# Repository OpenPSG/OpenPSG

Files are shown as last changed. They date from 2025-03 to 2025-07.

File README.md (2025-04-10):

# OpenPSG

A [FOSS](https://www.gnu.org/philosophy/free-sw.en.html) Polysomnography Platform For Sleep Research.

## Philosophy

* **Cost is Critical** (off-the-shelf, commodity components).
* **Less is More** (if one sensor can do the job of two, use it).
* **Easy to Use** (no complex setup/prep work).
* **Modular** (mix and match sensors).
* **Open Source** (hardware and software).
* **Open Data** (no proprietary formats).

## Disclaimer

OpenPSG is not intended to diagnose, treat, cure, or prevent any medical 
condition. It is designed for research purposes only and should not be used as 
a substitute for professional medical advice or care. Users are responsible for
ensuring compliance with the relevant regulations and standards in their region.

Hardware evaluation boards and kits are provided for use in engineering 
development, demonstration, or evaluation purposes only. They are not considered 
by the OpenPSG authors to be finished end-products fit for general consumer use.

All users are expected to have the necessary knowledge and experience to use the 
hardware and software safely and effectively. The OpenPSG authors are not 
responsible for any injuries, damages, or losses resulting from the use of the
hardware or software.

## License

All software is licensed under the [GNU Affero General Public License v3.0](https://www.gnu.org/licenses/agpl-3.0.html). 
All hardware designs are licensed under the [CERN Open Hardware License v2 - Strongly Reciprocal](https://ohwr.org/cern_ohl_s_v2.txt).

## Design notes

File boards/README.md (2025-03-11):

# Board Files

The boards are designed with/for KiCad v8.0.x

## JLCPCB Manufacturing and Assembly

### Gerbers and Drill Files

Follow the instructions here:

https://jlcpcb.com/help/article/how-to-generate-gerber-and-drill-files-in-kicad-8

### Bill of Materials (BOM)

In eeschema, go to `Tools` -> `Generate Bill of Materials`.

In the edit tab configure the fields as follows:

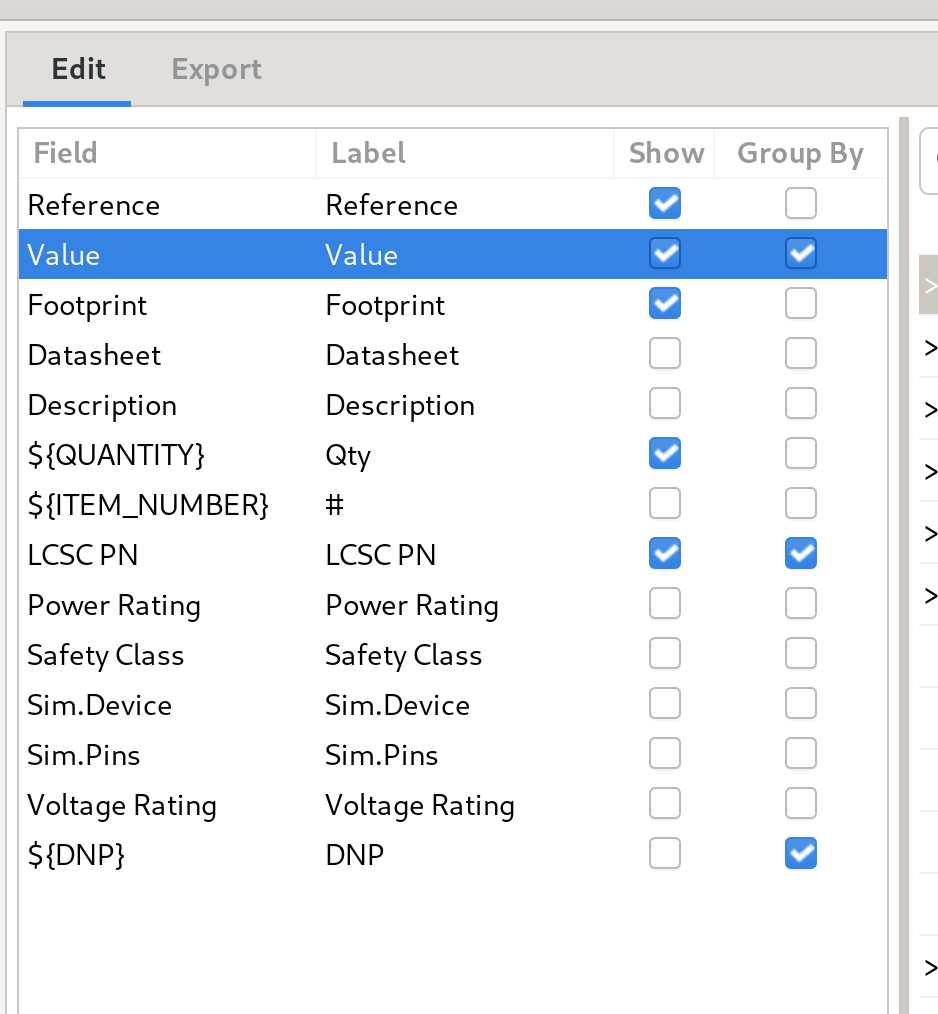
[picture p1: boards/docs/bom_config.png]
BOM configuration


Then click on `Generate` and save the file as `<board>-bom.csv` in the manufacturing files folder.

### Pick and Place (CPL)

In pcbnew, go to `File` -> `Fabrication Outputs` -> `Component Placement (.pos, .gbr)...`.

Configure the fields as follows:

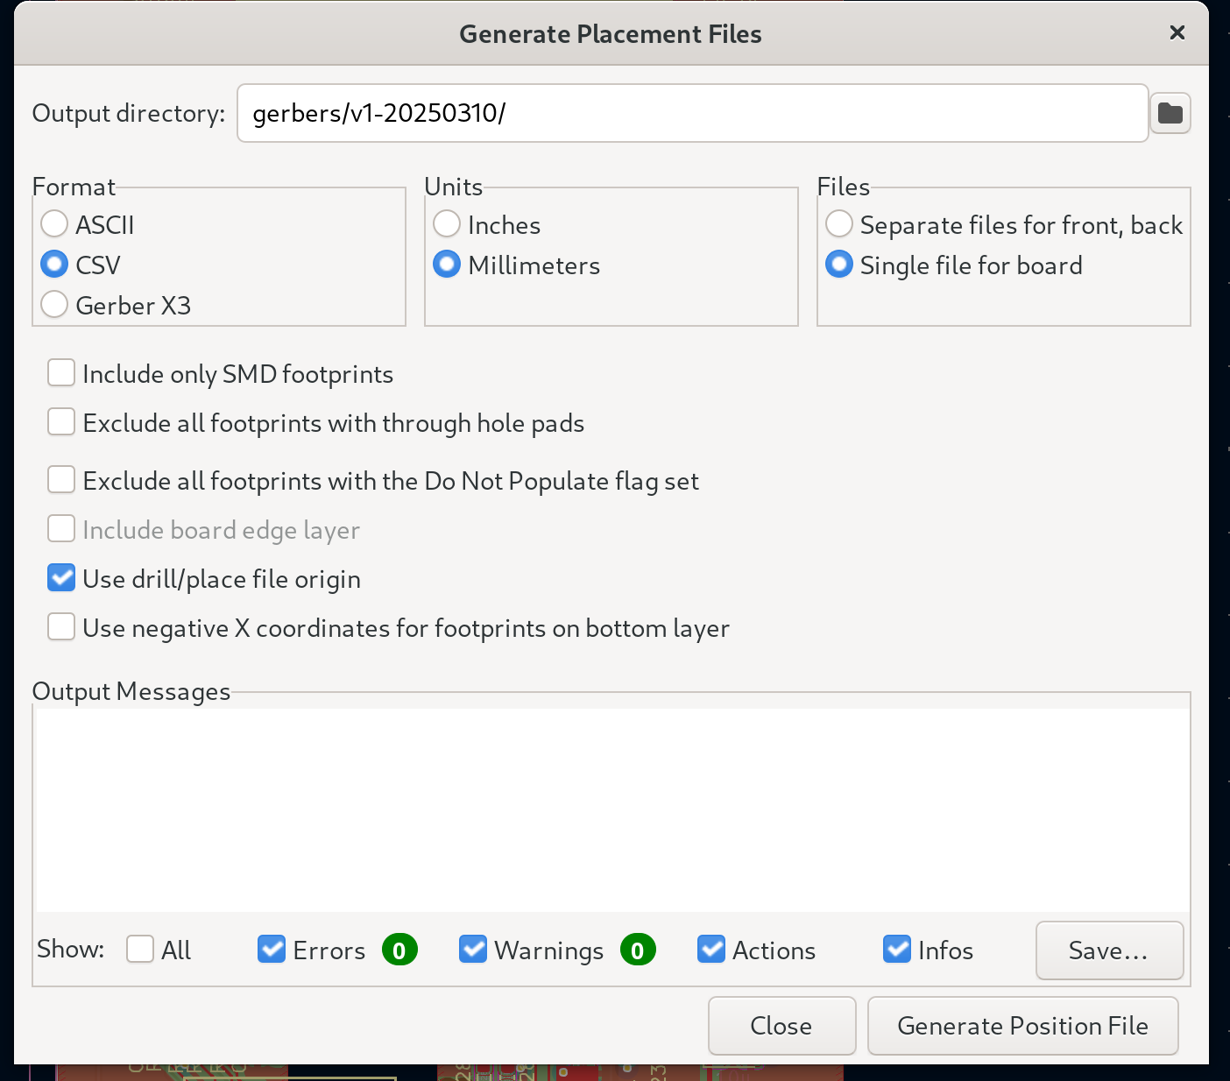
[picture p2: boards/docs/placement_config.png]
CPL configuration


Then click on `Generate`.

### Convert to JLCPCB Format

Use my [jlcfabtool](https://github.com/dpeckett/jlcfabtool) utility to convert the files to the JLCPCB format.

```sh
jlcfabtool bom convert <board>-bom.csv
jlcfabtool placement convert <board>-all-pos.csv
```

### Create the Archive

```sh
cd <board>
zip -r ../$(basename "$(pwd)").zip ./*
```

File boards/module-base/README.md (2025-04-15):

# Module Base

The starting point for all sensors / actuators.

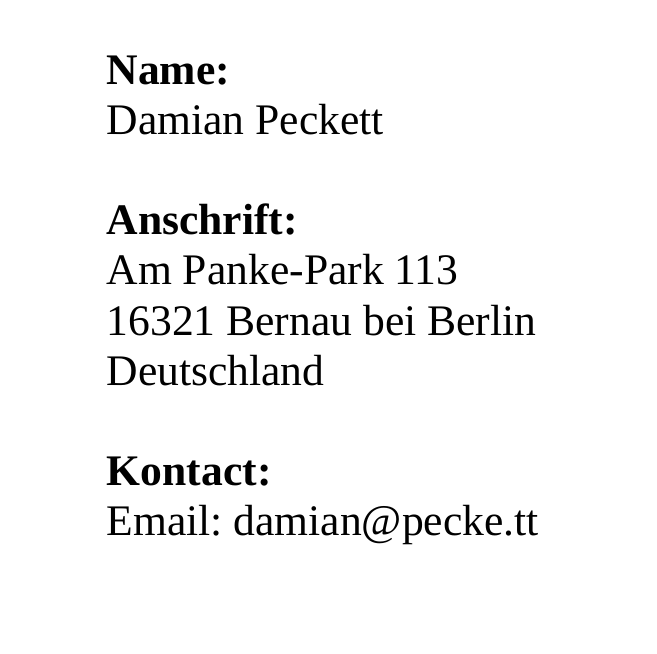
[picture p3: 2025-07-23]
public/images/contact.png

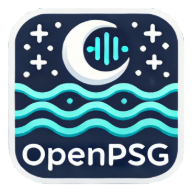
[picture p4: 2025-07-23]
public/web-app-manifest-192x192.png

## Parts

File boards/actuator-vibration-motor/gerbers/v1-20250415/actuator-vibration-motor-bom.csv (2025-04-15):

Reference | Value | Datasheet | Footprint | Qty | DNP | LCSC PN
C1,C4 | 1u | ~ | Capacitor_SMD:C_0402_1005Metric | 2 |  | C52923
C2,C3,C7 | 0.1u | ~ | Capacitor_SMD:C_0402_1005Metric | 3 |  | C1525
C5,C6 | 12p | ~ | Capacitor_SMD:C_0402_1005Metric | 2 |  | C1547
C8 | 1n | ~ | Capacitor_SMD:C_0402_1005Metric | 1 |  | C1523
D1 | 1N5819WS | https://datasheet.lcsc.com/lcsc/2204281430_Guangdong-Hottech-1N5819WS_C191023.pdf | Diode_SMD:D_SOD-323 | 1 |  | C191023
J1 | RS485 | ~ | Connector_JST:JST_PH_S4B-PH-K_1x04_P2.00mm_Horizontal | 1 |  | C2908636
J3 | Download | ~ | Connector_PinHeader_1.27mm:PinHeader_1x02_P1.27mm_Vertical | 1 |  | C703015
J4 | Vibration Motor | ~ | Connector_JST:JST_PH_S2B-PH-K_1x02_P2.00mm_Horizontal | 1 |  | C2908634
JP1 | Terminate | ~ | Jumper:SolderJumper-2_P1.3mm_Open_RoundedPad1.0x1.5mm | 1
Q1 | AO3400 | http://www.aosmd.com/pdfs/datasheet/AO3400A.pdf | Package_TO_SOT_SMD:SOT-23 | 1 |  | C20917
R1,R2 | 120 | ~ | Resistor_SMD:R_0402_1005Metric | 2 |  | C25079
U1 | AP2112K-3.3 | https://www.diodes.com/assets/Datasheets/AP2112.pdf | Package_TO_SOT_SMD:SOT-23-5 | 1 |  | C51118
U2 | COS13487E |  | Package_SO:SOP-8_3.9x4.9mm_P1.27mm | 1 |  | C22466040
U3 | STM32G031G8Ux | https://www.st.com/resource/en/datasheet/stm32g031g8.pdf | Package_DFN_QFN:QFN-28_4x4mm_P0.5mm | 1 |  | C432211
Y1 | 32.768k | ~ | Crystal:Crystal_SMD_3215-2Pin_3.2x1.5mm | 1 |  | C32346

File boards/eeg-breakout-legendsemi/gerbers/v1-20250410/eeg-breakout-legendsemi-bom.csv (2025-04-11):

Reference | Value | Datasheet | Footprint | Qty | DNP | LCSC PN
C1,C3,C5,C6,C9 | 1u | ~ | Capacitor_SMD:C_0402_1005Metric | 5 |  | C52923
C2,C4 | 0.1u | ~ | Capacitor_SMD:C_0402_1005Metric | 2 |  | C1525
C7,C10,C11,C12,C13,C14,C15,C16,C17,C18 | 1n | ~ | Capacitor_SMD:C_0402_1005Metric | 10 |  | C1523
C8 | 10u | ~ | Capacitor_SMD:C_0603_1608Metric | 1 |  | C19702
R1 | 1M | ~ | Resistor_SMD:R_0402_1005Metric | 1 |  | C26083
R2 | 100k | ~ | Resistor_SMD:R_0402_1005Metric | 1 |  | C25741
R3,R4,R5,R6,R7,R8,R9,R10,R11 | 2.2k | ~ | Resistor_SMD:R_0402_1005Metric | 9 |  | C25879
U1 | LH001-91Q40AR2 |  | Package_DFN_QFN:QFN-40-1EP_5x5mm_P0.4mm_EP3.6x3.6mm | 1 |  | C42459077

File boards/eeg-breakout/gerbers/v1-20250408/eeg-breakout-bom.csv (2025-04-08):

Reference | Value | Datasheet | Footprint | Qty | DNP | LCSC PN
C1,C4,C13 | 10u | ~ | Capacitor_SMD:C_0603_1608Metric | 3 |  | C19702
C2,C3,C5,C6,C11,C12,C16 | 0.1u | ~ | Capacitor_SMD:C_0402_1005Metric | 7 |  | C1525
C7,C8,C14,C15 | 1u | ~ | Capacitor_SMD:C_0402_1005Metric | 4 |  | C52923
C9,C10 | 4.7n | ~ | Capacitor_SMD:C_0402_1005Metric | 2 |  | C1538
C17,C18,C19,C20,C21,C22 | 1n | ~ | Capacitor_SMD:C_0402_1005Metric | 6 |  | C1523
FB1,FB2 | FerriteBead_Small | ~ | Inductor_SMD:L_0603_1608Metric | 2 |  | C19330
R1,R2 | 4.7k | ~ | Resistor_SMD:R_0402_1005Metric | 2 |  | C25900
R3 | 1M | ~ | Resistor_SMD:R_0402_1005Metric | 1 |  | C26083
R4,R5,R6,R7,R8 | 2.2k | ~ | Resistor_SMD:R_0402_1005Metric | 5 |  | C25879
U1 | ISOW7741 | https://www.ti.com/lit/ds/symlink/isow7741.pdf | Package_SO:SOIC-20W_7.5x12.8mm_P1.27mm | 1 |  | C5216399
U2 | ADS1292IRSMR | ADS1292IRSMR | VQFN-32-1EP_4x4mm_P0.4mm_EP2.8x2.8mm | 1 |  | C544416

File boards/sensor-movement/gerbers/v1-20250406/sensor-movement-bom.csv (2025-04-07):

Reference | Value | Datasheet | Footprint | Qty | DNP | LCSC PN
C1,C3,C4,C5,C9,C10,C12 | 0.1u | ~ | Capacitor_SMD:C_0402_1005Metric | 7 |  | C1525
C2,C6,C7 | 1u | ~ | Capacitor_SMD:C_0402_1005Metric | 3 |  | C52923
C8,C11 | 12p | ~ | Capacitor_SMD:C_0402_1005Metric | 2 |  | C1547
J1 | Conn_01x04 | ~ | Connector_JST:JST_PH_S4B-PH-K_1x04_P2.00mm_Horizontal | 1 |  | C2908636
JP1 | Terminate | ~ | Jumper:SolderJumper-2_P1.3mm_Open_RoundedPad1.0x1.5mm | 1
R1 | 10k | ~ | Resistor_SMD:R_0402_1005Metric | 1 |  | C25744
R2,R3 | 2.2k | ~ | Resistor_SMD:R_0402_1005Metric | 2 |  | C25879
R4 | 120 | ~ | Resistor_SMD:R_0402_1005Metric | 1 |  | C25079
R5 | 200k | ~ | Resistor_SMD:R_0402_1005Metric | 1 |  | C25764
R6,R7 | 4.7k | ~ | Resistor_SMD:R_0402_1005Metric | 2 |  | C25900
U1 | PCA9306DCUR | https://www.nxp.com/docs/en/data-sheet/PCA9306.pdf | Package_SO:VSSOP-8_2.4x2.1mm_P0.5mm | 1 |  | C33196
U2 | ICM-20948 | http://www.invensense.com/wp-content/uploads/2016/06/DS-000189-ICM-20948-v1.3.pdf | Sensor_Motion:InvenSense_QFN-24_3x3mm_P0.4mm | 1 |  | C726001
U3 | AP2112K-3.3 | https://www.diodes.com/assets/Datasheets/AP2112.pdf | Package_TO_SOT_SMD:SOT-23-5 | 1 |  | C51118
U4 | AP2112K-1.8 | https://www.diodes.com/assets/Datasheets/AP2112.pdf | Package_TO_SOT_SMD:SOT-23-5 | 1 |  | C176944
U5 | SP3072EEN-L | SP3072EEN-L | Package_SO:SOP-8_3.9x4.9mm_P1.27mm | 1 |  | C2692300
U6 | STM32G031G8Ux | https://www.st.com/resource/en/datasheet/stm32g031g8.pdf | Package_DFN_QFN:QFN-28_4x4mm_P0.5mm | 1 |  | C432211
Y1 | 32.768k | ~ | Crystal:Crystal_SMD_3215-2Pin_3.2x1.5mm | 1 |  | C32346

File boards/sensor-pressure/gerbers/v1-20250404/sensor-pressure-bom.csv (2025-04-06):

Reference | Value | Datasheet | Footprint | Qty | DNP | LCSC PN
C1,C2,C3,C4,C5,C9,C10 | 0.1u | ~ | Capacitor_SMD:C_0402_1005Metric | 7 |  | C1525
C6,C7 | 1u | ~ | Capacitor_SMD:C_0402_1005Metric | 2 |  | C52923
C8,C11 | 12p | ~ | Capacitor_SMD:C_0402_1005Metric | 2 |  | C1547
J1 | Conn_01x04 | ~ | Connector_JST:JST_PH_S4B-PH-K_1x04_P2.00mm_Horizontal | 1 |  | C2908636
JP1 | Terminate | ~ | Jumper:SolderJumper-2_P1.3mm_Open_RoundedPad1.0x1.5mm | 1
L1 | 10u | ~ | Inductor_SMD:L_0805_2012Metric | 1 |  | C1046
R1 | 330 | ~ | Resistor_SMD:R_0402_1005Metric | 1 |  | C25104
R2,R3,R4 | 120 | ~ | Resistor_SMD:R_0402_1005Metric | 3 |  | C25079
U1 | GZP160-040S |  | footprints:GZP160-040S | 1 |  | C3037979
U2 | HX710B |  | Package_SO:SOP-8_3.9x4.9mm_P1.27mm | 1 |  | C68417
U3 | AP2112K-3.3 | https://www.diodes.com/assets/Datasheets/AP2112.pdf | Package_TO_SOT_SMD:SOT-23-5 | 1 |  | C51118
U4 | TL431 | http://www.ti.com/lit/ds/symlink/tl431.pdf | Package_TO_SOT_SMD:SOT-23 | 1 |  | C23892
U5 | SP3072EEN-L | SP3072EEN-L | Package_SO:SOP-8_3.9x4.9mm_P1.27mm | 1 |  | C2692300
U6 | STM32G031G8Ux | https://www.st.com/resource/en/datasheet/stm32g031g8.pdf | Package_DFN_QFN:QFN-28_4x4mm_P0.5mm | 1 |  | C432211
Y1 | 32.768k | ~ | Crystal:Crystal_SMD_3215-2Pin_3.2x1.5mm | 1 |  | C32346

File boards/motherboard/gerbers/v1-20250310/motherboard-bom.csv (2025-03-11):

Reference | Value | Footprint | Qty | LCSC PN
C1,C2,C3,C4,C7,C10,C11,C12,C13,C14,C15,C16,C18,C20,C22,C29,C37,C39,C40,C41,C42,C43,C44,C45,C48,C49 | 100n | Capacitor_SMD:C_0603_1608Metric | 26 | C14663
C5,C6 | 20p | Capacitor_SMD:C_0603_1608Metric | 2 | C1648
C8,C9 | 2.2u | Capacitor_SMD:C_0603_1608Metric | 2 | C23630
C17,C19,C30 | 10u | Capacitor_SMD:C_0603_1608Metric | 3 | C96446
C21,C32 | 12p | Capacitor_SMD:C_0603_1608Metric | 2 | C38523
C23,C26,C27 | 100n | Capacitor_SMD:C_0603_1608Metric | 3 | C15725
C24 | 22n | Capacitor_SMD:C_0603_1608Metric | 1 | C21122
C25 | 22u | Capacitor_SMD:CP_Elec_6.3x7.7 | 1 | C267472
C28 | 330p | Capacitor_SMD:C_0603_1608Metric | 1 | C126579
C31 | 10n | Capacitor_SMD:C_0603_1608Metric | 1 | C107059
C33 | 680p | Capacitor_SMD:C_0603_1608Metric | 1 | C1630
C34,C46,C47 | 47u | Capacitor_SMD:C_0603_1608Metric | 3 | C96123
C35 | 100p | Capacitor_SMD:C_0603_1608Metric | 1 | C14858
C36 | 8.2n | Capacitor_SMD:C_0603_1608Metric | 1 | C1322360
C38 | 1u | Capacitor_SMD:C_0603_1608Metric | 1 | C15849
CY1 | 2.2n | Capacitor_THT:C_Disc_D10.5mm_W5.0mm_P10.00mm | 1 | C499511
D2 | SMAJ58A | Diode_SMD:D_SMA | 1 | C110521
D3 | S1B-13-F | Diode_SMD:D_SMA | 1 | C156295
D4 | BAS16W | Package_TO_SOT_SMD:SOT-323_SC-70 | 1 | C56624
D5 | SS34 | Diode_SMD:D_SMA | 1 | C8678
D6 | BAV99 | Package_TO_SOT_SMD:SOT-23 | 1 | C2500
J2 | Boot Selection | Connector_PinHeader_2.54mm:PinHeader_1x03_P2.54mm_Vertical | 1 | C2894926
J3,J6 | Arduino Connector | Connector_PinSocket_2.54mm:PinSocket_1x08_P2.54mm_Vertical | 2 | C2897371
J4 | Arduino Connector | Connector_PinSocket_2.54mm:PinSocket_1x06_P2.54mm_Vertical | 1 | C2897369
J5 | Arduino Connector | Connector_PinSocket_2.54mm:PinSocket_1x10_P2.54mm_Vertical | 1 | C2897373
J7 | JTAG | Connector_IDC:IDC-Header_2x10_P2.54mm_Vertical | 1 | C5372868
J8 | HY931147C | footprints:HY931147C | 1 | C91754
L1 | 4.7u | Inductor_SMD:L_0805_2012Metric | 1 | C114862
L2 | 4.7u | Inductor_SMD:L_1008_2520Metric | 1 | C82314
Q1 | FDC86244 | Package_TO_SOT_SMD:SuperSOT-6 | 1 | C3290085
R1,R4,R5,R6,R26,R30,R38,R41,R42,R43,R44,R45 | 51 | Resistor_SMD:R_0603_1608Metric | 12 | C23197
R2,R23 | 510 | Resistor_SMD:R_0603_1608Metric | 2 | C23193
R7,R8,R10,R11,R12,R13,R14,R15,R35 | 10k | Resistor_SMD:R_0603_1608Metric | 9 | C25804
R9 | 1M | Resistor_SMD:R_0603_1608Metric | 1 | C22935
R18 | 82k | Resistor_SMD:R_0603_1608Metric | 1 | C23254
R20 | 24.9k | Resistor_SMD:R_0603_1608Metric | 1 | C2930080
R21 | 62k | Resistor_SMD:R_0603_1608Metric | 1 | C23221
R22 | 1.27k | Resistor_SMD:R_0603_1608Metric | 1 | C2930048
R25,R37,R39,R40,R46,R47 | 2.2k | Resistor_SMD:R_0603_1608Metric | 6 | C4190
R27 | 0.56 | Resistor_SMD:R_1206_3216Metric | 1 | C2907358
R28 | 82 | Resistor_SMD:R_0603_1608Metric | 1 | C23255
R29 | 51k | Resistor_SMD:R_0603_1608Metric | 1 | C23196
R31 | 20 | Resistor_SMD:R_0603_1608Metric | 1 | C22950
R32 | 1k | Resistor_SMD:R_0603_1608Metric | 1 | C21190
R33 | 47k | Resistor_SMD:R_0603_1608Metric | 1 | C25819
R34 | 15k | Resistor_SMD:R_0603_1608Metric | 1 | C22809
R36 | 20k | Resistor_SMD:R_0603_1608Metric | 1 | C4184
R48 | 4.87k | Resistor_SMD:R_0603_1608Metric | 1 | C2998129
SW1 | Reset | Button_Switch_SMD:SW_Tactile_SPST_NO_Straight_CK_PTS636Sx25SMTRLFS | 1 | C318938
T1 | HR051067 | footprints:XFMR-SMD_HR051067 | 1 | C93830
U1 | STM32F407VETx | Package_QFP:LQFP-100_14x14mm_P0.5mm | 1 | C28730
U2 | TPS23753APWR | Package_SO:TSSOP-14_4.4x5mm_P0.65mm | 1 | C92115
U3 | FOD817ASD | footprints:SOIC254P1016X385-4N | 1 | C241830
U4 | TLV431ASN1 | Package_TO_SOT_SMD:SOT-23-3 | 1 | C127592
U5 | DP83848I | Package_QFP:LQFP-48_7x7mm_P0.5mm | 1 | C12082
U6 | AMS1117-3.3 | Package_TO_SOT_SMD:SOT-223-3_TabPin2 | 1 | C6186
X1 | 50M | Oscillator:Oscillator_SMD_SeikoEpson_SG8002LB-4Pin_5.0x3.2mm | 1 | C7429728
Y1 | 8M | Crystal:Crystal_SMD_5032-2Pin_5.0x3.2mm | 1 | C115962
Y2 | 32.768k | Crystal:Crystal_SMD_3215-2Pin_3.2x1.5mm | 1 | C32346

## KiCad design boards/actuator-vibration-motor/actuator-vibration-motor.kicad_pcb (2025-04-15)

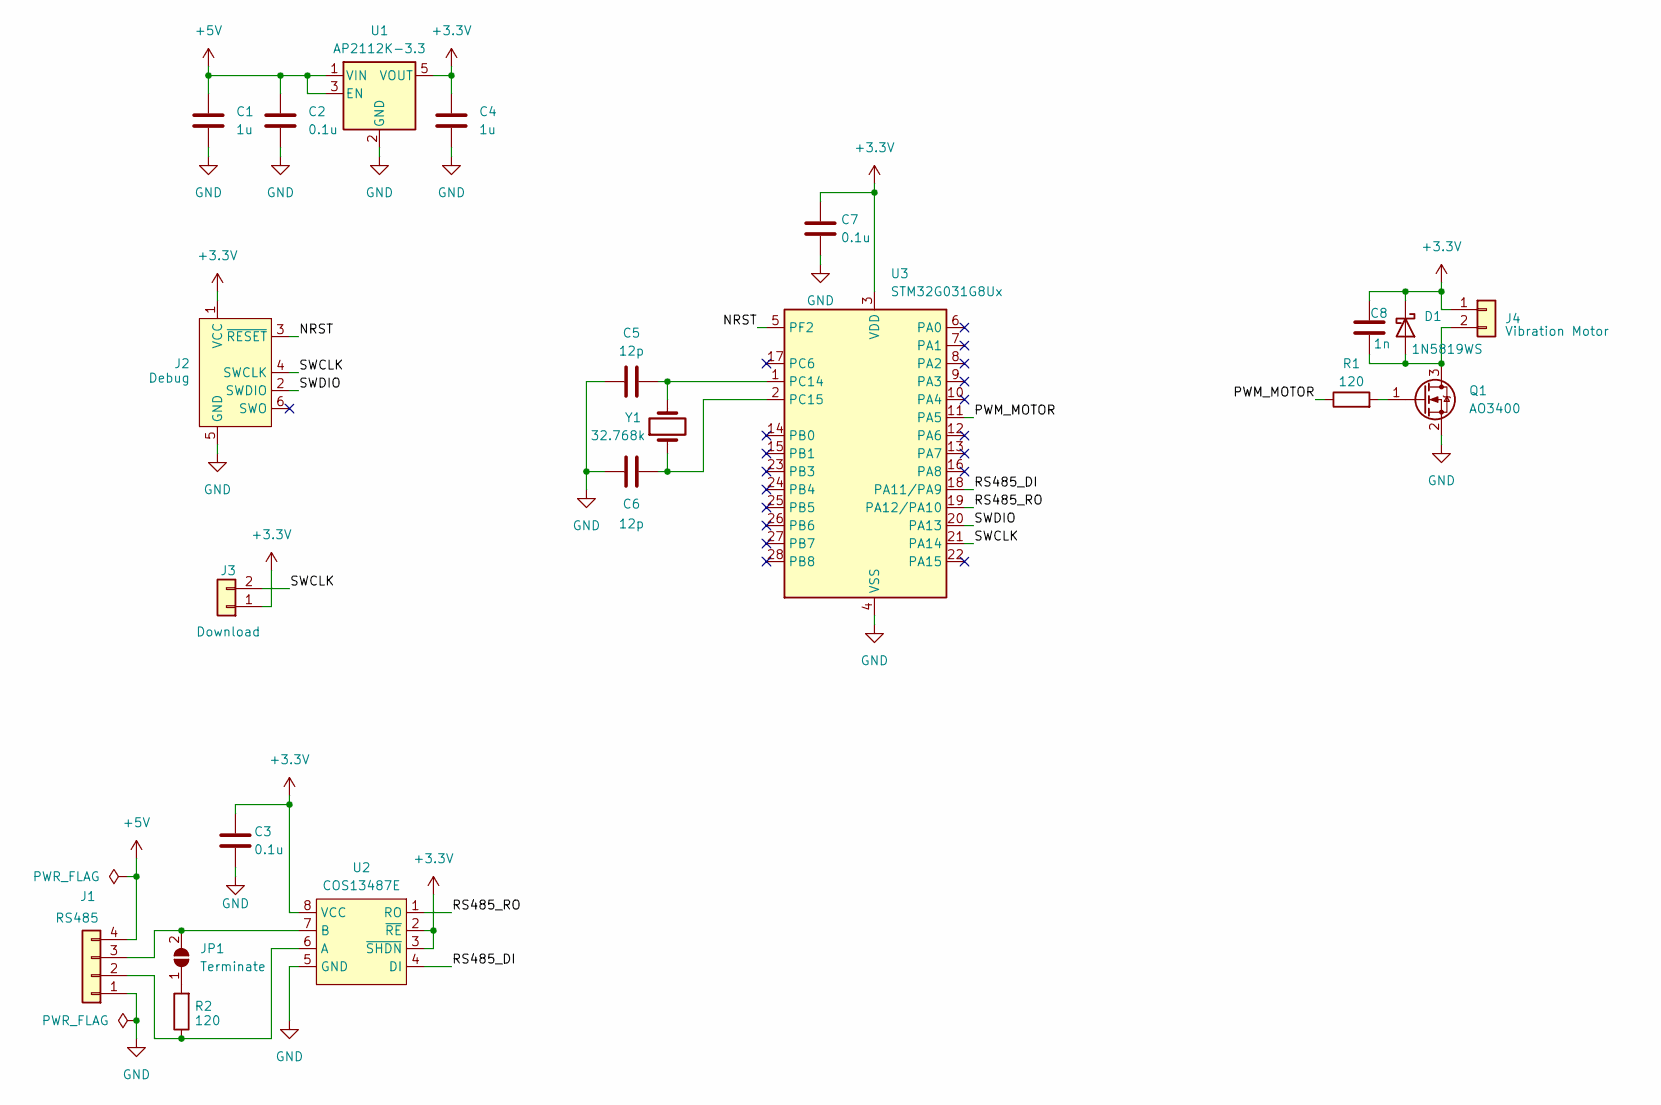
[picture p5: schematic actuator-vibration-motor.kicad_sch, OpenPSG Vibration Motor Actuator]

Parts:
C1, C4: 1u; C_0402_1005Metric; LCSC PN C52923
C2, C3, C7: 0.1u; C_0402_1005Metric; LCSC PN C1525
C5, C6: 12p; C_0402_1005Metric; LCSC PN C1547
C8: 1n; C_0402_1005Metric; LCSC PN C1523
D1: 1N5819WS; D_SOD-323; LCSC PN C191023
J1: RS485; JST_PH_S4B-PH-K_1x04_P2.00mm_Horizontal; LCSC PN C2908636
J2: Debug; Tag-Connect_TC2030-IDC-NL_2x03_P1.27mm_Vertical
J3: Download; PinHeader_1x02_P1.27mm_Vertical; LCSC PN C703015
J4: Vibration Motor; JST_PH_S2B-PH-K_1x02_P2.00mm_Horizontal; LCSC PN C2908634
JP1: Terminate; SolderJumper-2_P1.3mm_Open_RoundedPad1.0x1.5mm
Q1: AO3400; SOT-23; LCSC PN C20917
R1, R2: 120; R_0402_1005Metric; LCSC PN C25079
U1: AP2112K-3.3; SOT-23-5; LCSC PN C51118
U2: COS13487E; SOP-8_3.9x4.9mm_P1.27mm; LCSC PN C22466040
U3: STM32G031G8Ux; QFN-28_4x4mm_P0.5mm; LCSC PN C432211
Y1: 32.768k; Crystal_SMD_3215-2Pin_3.2x1.5mm; LCSC PN C32346

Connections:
+3.3V: C3.1, C4.1, C7.1, C8.1, D1.1 (K), J2.1 (VCC), J3.1, J4.1, U1.5 (VOUT), U2.2 (~RE), U2.3 (~SHDN), U2.8 (VCC), U3.3 (VDD)
+5V: C1.1, C2.1, J1.4, U1.1 (VIN), U1.3 (EN)
/NRST: J2.3 (~RESET), U3.5 (PF2)
/PWM_MOTOR: R1.1, U3.11 (PA5)
/RS485_DI: U2.4 (DI), U3.18 (PA11/PA9)
/RS485_RO: U2.1 (RO), U3.19 (PA12/PA10)
/SWCLK: J2.4 (SWCLK), J3.2, U3.21 (PA14)
/SWDIO: J2.2 (SWDIO), U3.20 (PA13)
GND: C1.2, C2.2, C3.2, C4.2, C5.2, C6.1, C7.2, J1.1, J2.5 (GND), Q1.2 (S), U1.2 (GND), U2.5 (GND), U3.4 (VSS)
unnamed: C8.2, D1.2 (A), J4.2, Q1.3 (D)
unnamed: J1.2, R2.1, U2.6 (A)
unnamed: J1.3, JP1.2 (B), U2.7 (B)
unnamed: JP1.1 (A), R2.2
unnamed: Q1.1 (G), R1.2
unnamed: C5.1, U3.1 (PC14), Y1.2
unnamed: C6.2, U3.2 (PC15), Y1.1

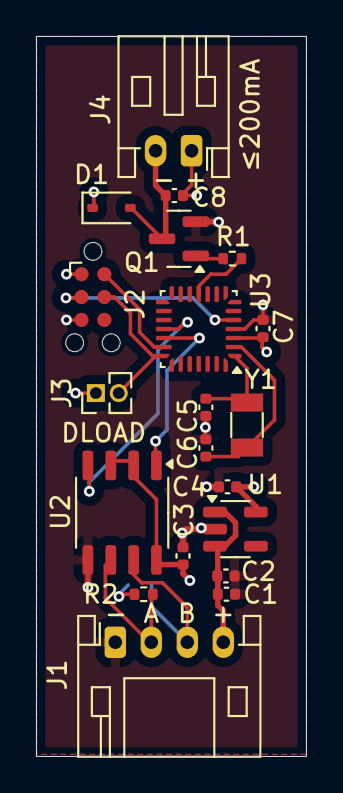
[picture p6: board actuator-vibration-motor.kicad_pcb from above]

Board: 4 copper layers, 15.0 x 40.0 mm, 21 parts (1 on the bottom side), 16 nets.

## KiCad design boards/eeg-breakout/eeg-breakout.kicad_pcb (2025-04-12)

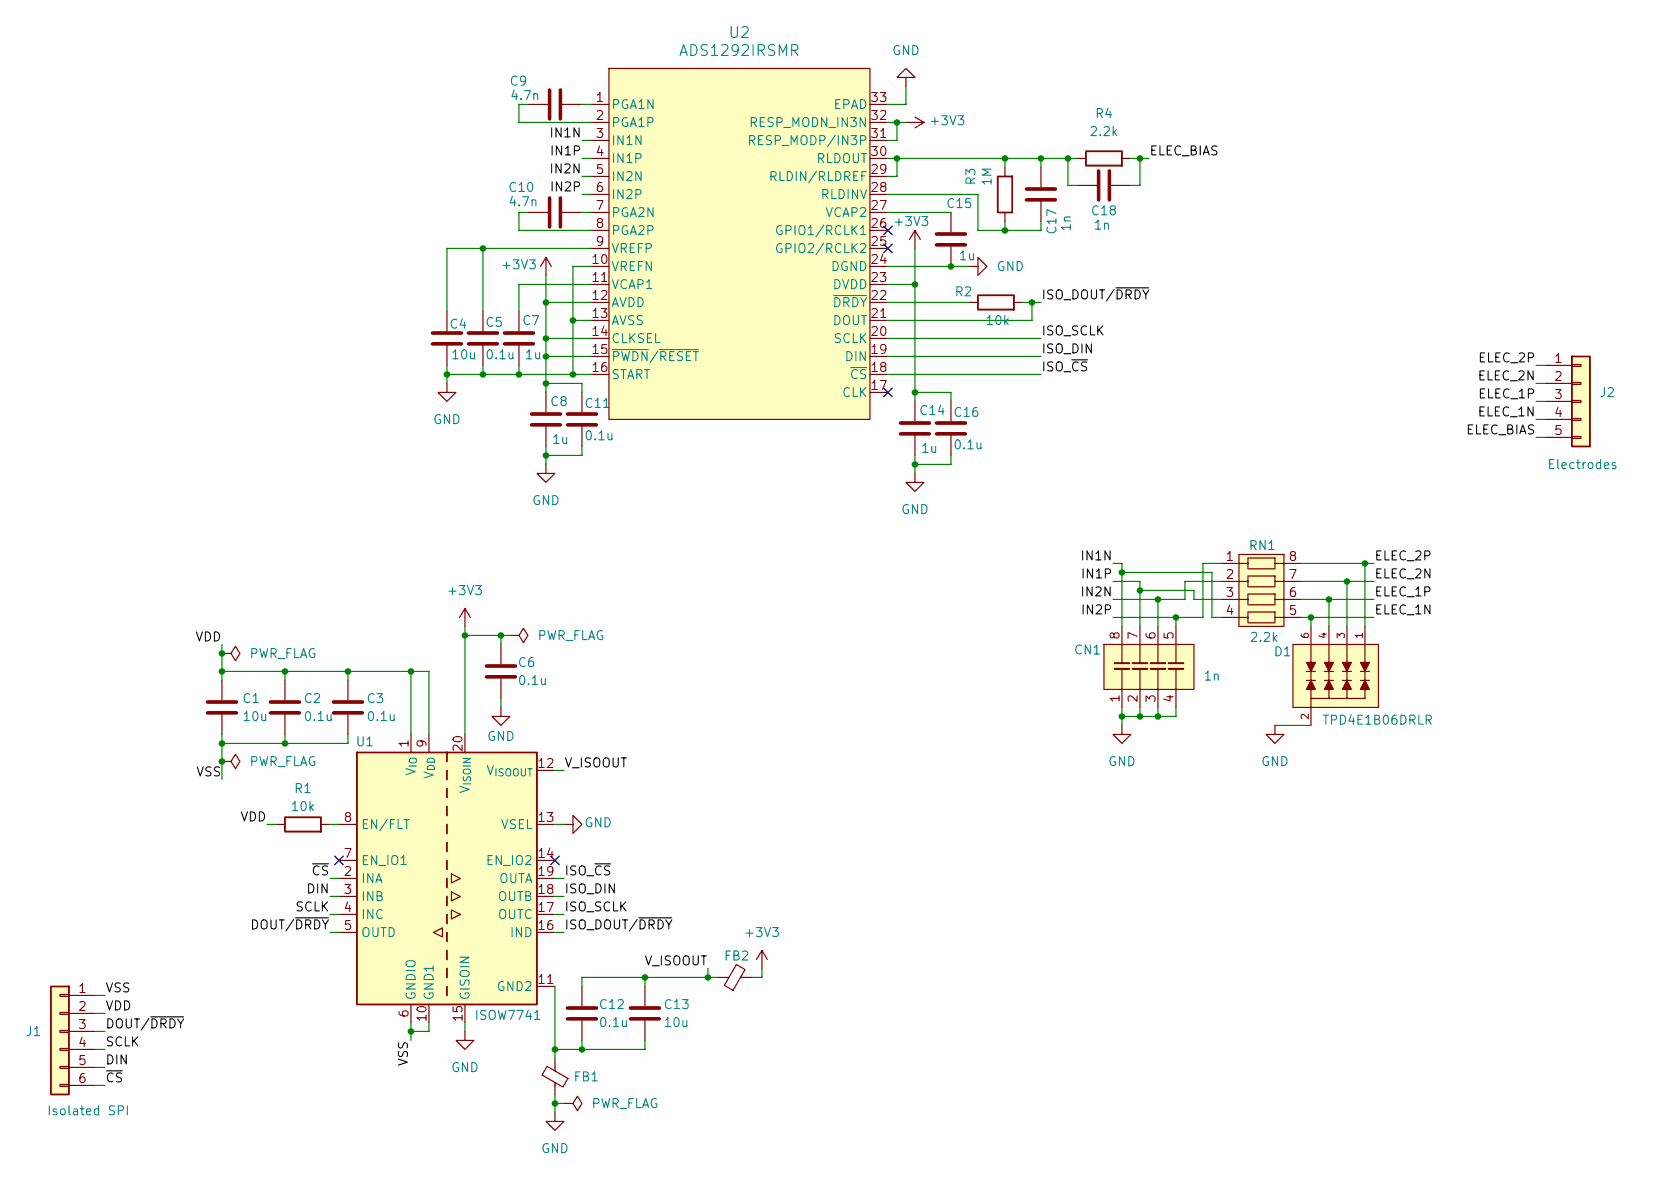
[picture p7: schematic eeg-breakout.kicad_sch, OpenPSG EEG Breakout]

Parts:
C1, C4, C13: 10u; C_0603_1608Metric; LCSC PN C19702
C2, C3, C5, C6, C11, C12, C16: 0.1u; C_0402_1005Metric; LCSC PN C1525
C7, C8, C14, C15: 1u; C_0402_1005Metric; LCSC PN C52923
C9, C10: 4.7n; C_0402_1005Metric; LCSC PN C1538
C17, C18: 1n; C_0402_1005Metric; LCSC PN C1523
CN1: 1n; R_Array_Convex_4x0612; LCSC PN C2649771
D1: TPD4E1B06DRLR; SOT-563; LCSC PN C1972953
FB1, FB2: FerriteBead_Small; L_0603_1608Metric; LCSC PN C19330
J1: Isolated SPI; PinHeader_1x06_P2.54mm_Horizontal
J2: Electrodes; PinHeader_1x05_P2.54mm_Horizontal
R1, R2: 10k; R_0402_1005Metric; LCSC PN C25744
R3: 1M; R_0402_1005Metric; LCSC PN C26083
R4: 2.2k; R_0402_1005Metric; LCSC PN C25879
RN1: 2.2k; R_Array_Convex_4x0402; LCSC PN C326864
U1: ISOW7741; SOIC-20W_7.5x12.8mm_P1.27mm; LCSC PN C5216399
U2: ADS1292IRSMR; VQFN-32-1EP_4x4mm_P0.4mm_EP2.8x2.8mm; LCSC PN C544416

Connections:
+3V3: C6.1, C8.1, C11.1, C14.1, C16.1, FB2.2, U1.20 (V_{ISOIN}), U2.12 (AVDD), U2.14 (CLKSEL), U2.15 (~PWDN/~RESET), U2.23 (DVDD), U2.31 (RESP_MODP/IN3P), U2.32 (RESP_MODN_IN3N)
/DIN: J1.5, U1.3 (INB)
/DOUT/~DRDY: J1.3, U1.5 (OUTD)
/ELEC_1N: D1.6, J2.4, RN1.5
/ELEC_1P: D1.4, J2.3, RN1.6
/ELEC_2N: D1.3, J2.2, RN1.7
/ELEC_2P: D1.1, J2.1, RN1.8
/ELEC_BIAS: C18.2, J2.5, R4.2
/IN1N: CN1.8, RN1.4, U2.3 (IN1N)
/IN1P: CN1.7, RN1.3, U2.4 (IN1P)
/IN2N: CN1.6, RN1.2, U2.5 (IN2N)
/IN2P: CN1.5, RN1.1, U2.6 (IN2P)
/ISO_DIN: U1.18 (OUTB), U2.19 (DIN)
/ISO_DOUT/~DRDY: R2.2, U1.16 (IND), U2.21 (DOUT)
/ISO_SCLK: U1.17 (OUTC), U2.20 (SCLK)
/ISO_~CS: U1.19 (OUTA), U2.18 (~CS)
/SCLK: J1.4, U1.4 (INC)
/VDD: C1.1, C2.1, C3.1, J1.2, R1.1, U1.1 (V_{IO}), U1.9 (V_{DD})
/VSS: C1.2, C2.2, C3.2, J1.1, U1.6 (GNDIO), U1.10 (GND1)
/V_ISOOUT: C12.1, C13.1, FB2.1, U1.12 (V_{ISOOUT})
/~CS: J1.6, U1.2 (INA)
GND: C4.2, C5.2, C6.2, C7.1, C8.2, C11.2, C14.2, C15.2, C16.2, CN1.1, CN1.2, CN1.3, CN1.4, D1.2, FB1.1, U1.13 (VSEL), U1.15 (GISOIN), U2.10 (VREFN), U2.13 (AVSS), U2.16 (START), U2.24 (DGND), U2.33 (EPAD)
unnamed: R1.2, U1.8 (EN/FLT)
unnamed: C12.2, C13.2, FB1.2, U1.11 (GND2)
unnamed: C9.2, U2.1 (PGA1N)
unnamed: C9.1, U2.2 (PGA1P)
unnamed: C10.2, U2.7 (PGA2N)
unnamed: C10.1, U2.8 (PGA2P)
unnamed: C17.1, R3.1, U2.28 (RLDINV)
unnamed: C17.2, C18.1, R3.2, R4.1, U2.29 (RLDIN/RLDREF), U2.30 (RLDOUT)
unnamed: C7.2, U2.11 (VCAP1)
unnamed: C15.1, U2.27 (VCAP2)
unnamed: C4.1, C5.1, U2.9 (VREFP)
unnamed: R2.1, U2.22 (~DRDY)

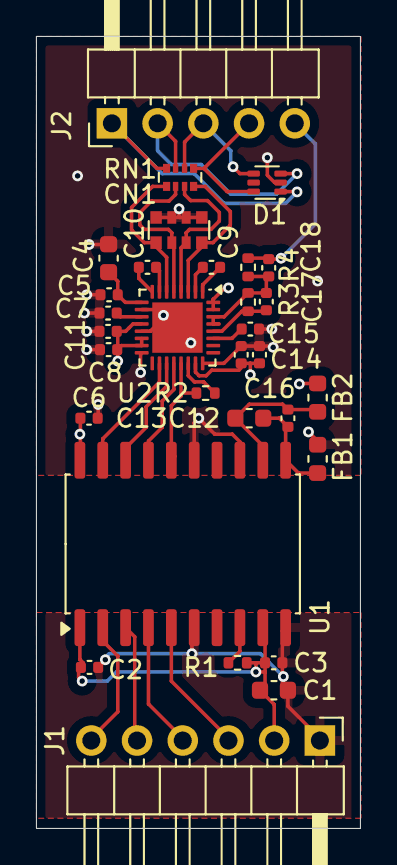
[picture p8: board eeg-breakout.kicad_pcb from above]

Board: 4 copper layers, 18.0 x 44.0 mm, 31 parts (0 on the bottom side), 34 nets.

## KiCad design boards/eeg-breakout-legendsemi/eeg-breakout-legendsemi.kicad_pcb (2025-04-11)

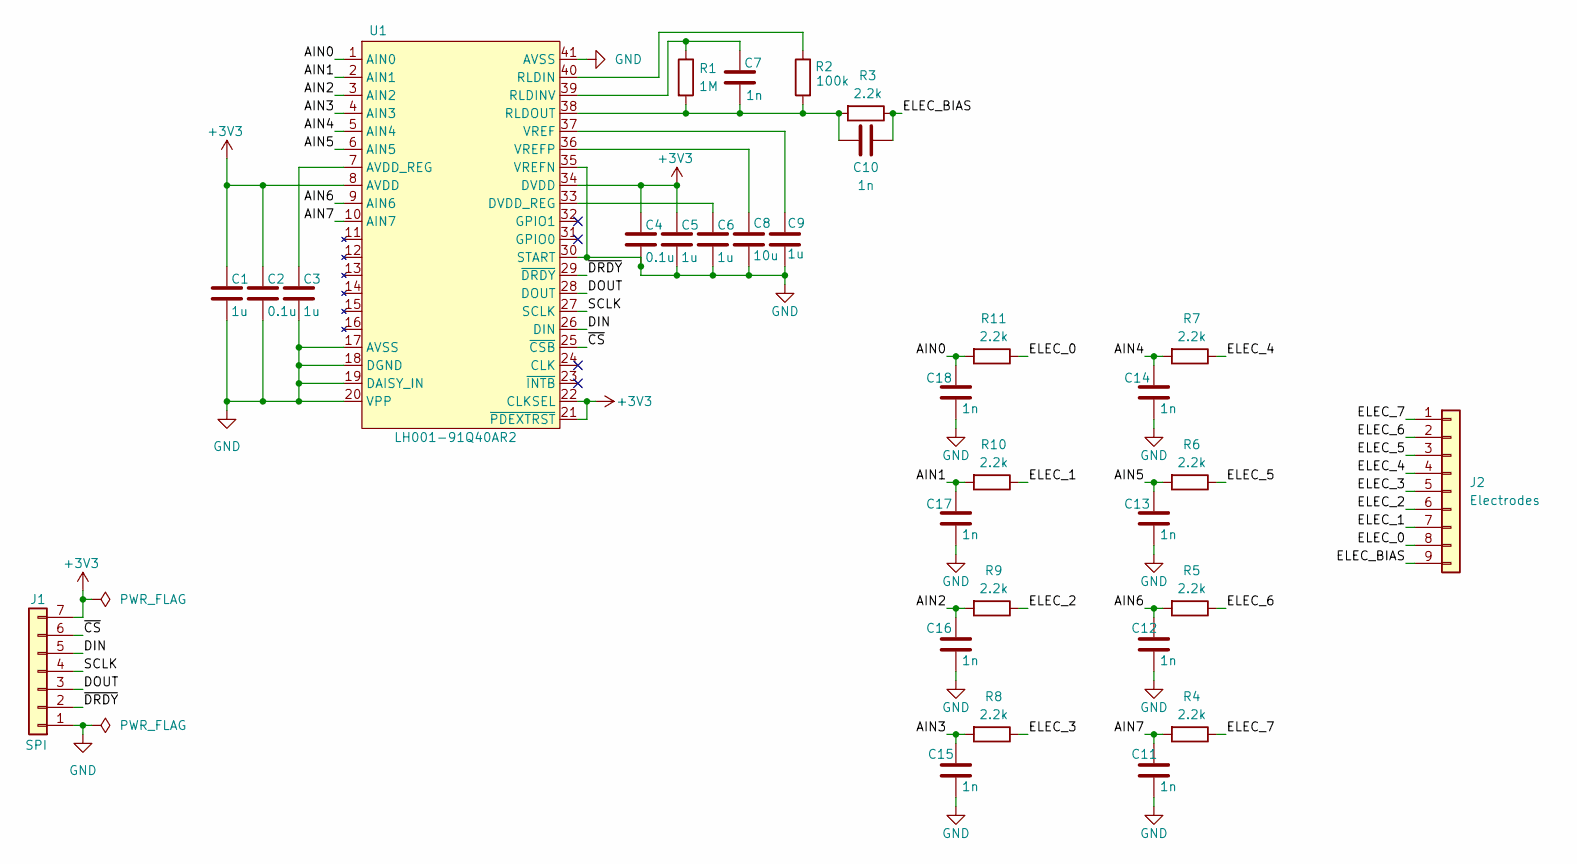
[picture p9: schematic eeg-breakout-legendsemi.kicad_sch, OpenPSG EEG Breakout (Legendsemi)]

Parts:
C1, C3, C5, C6, C9: 1u; C_0402_1005Metric; LCSC PN C52923
C2, C4: 0.1u; C_0402_1005Metric; LCSC PN C1525
C7, C10, C11, C12, C13, C14, C15, C16, C17, C18: 1n; C_0402_1005Metric; LCSC PN C1523
C8: 10u; C_0603_1608Metric; LCSC PN C19702
J1: SPI; PinHeader_1x07_P2.54mm_Horizontal
J2: Electrodes; PinHeader_1x09_P2.54mm_Horizontal
R1: 1M; R_0402_1005Metric; LCSC PN C26083
R2: 100k; R_0402_1005Metric; LCSC PN C25741
R3, R4, R5, R6, R7, R8, R9, R10, R11: 2.2k; R_0402_1005Metric; LCSC PN C25879
U1: LH001-91Q40AR2; QFN-40-1EP_5x5mm_P0.4mm_EP3.6x3.6mm; LCSC PN C42459077

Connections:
+3V3: C1.1, C2.1, C4.1, C5.1, J1.7, U1.8 (AVDD), U1.21 (~PDEXTRST), U1.22 (CLKSEL), U1.34 (DVDD)
/AIN0: C18.1, R11.2, U1.1 (AIN0)
/AIN1: C17.1, R10.2, U1.2 (AIN1)
/AIN2: C16.1, R9.2, U1.3 (AIN2)
/AIN3: C15.1, R8.2, U1.4 (AIN3)
/AIN4: C14.1, R7.2, U1.5 (AIN4)
/AIN5: C13.1, R6.2, U1.6 (AIN5)
/AIN6: C12.1, R5.2, U1.9 (AIN6)
/AIN7: C11.1, R4.2, U1.10 (AIN7)
/DIN: J1.5, U1.26 (DIN)
/DOUT: J1.3, U1.28 (DOUT)
/ELEC_0: J2.8, R11.1
/ELEC_1: J2.7, R10.1
/ELEC_2: J2.6, R9.1
/ELEC_3: J2.5, R8.1
/ELEC_4: J2.4, R7.1
/ELEC_5: J2.3, R6.1
/ELEC_6: J2.2, R5.1
/ELEC_7: J2.1, R4.1
/ELEC_BIAS: C10.1, J2.9, R3.1
/SCLK: J1.4, U1.27 (SCLK)
/~CS: J1.6, U1.25 (~CSB)
/~DRDY: J1.2, U1.29 (~DRDY)
GND: C1.2, C2.2, C3.2, C4.2, C5.2, C6.2, C8.2, C9.2, C11.2, C12.2, C13.2, C14.2, C15.2, C16.2, C17.2, C18.2, J1.1, U1.17 (AVSS), U1.18 (DGND), U1.19 (DAISY_IN), U1.20 (VPP), U1.30 (START), U1.35 (VREFN), U1.41 (AVSS)
unnamed: C3.1, U1.7 (AVDD_REG)
unnamed: C6.1, U1.33 (DVDD_REG)
unnamed: R2.1, U1.40 (RLDIN)
unnamed: C7.1, R1.1, U1.39 (RLDINV)
unnamed: C7.2, C10.2, R1.2, R2.2, R3.2, U1.38 (RLDOUT)
unnamed: C9.1, U1.37 (VREF)
unnamed: C8.1, U1.36 (VREFP)

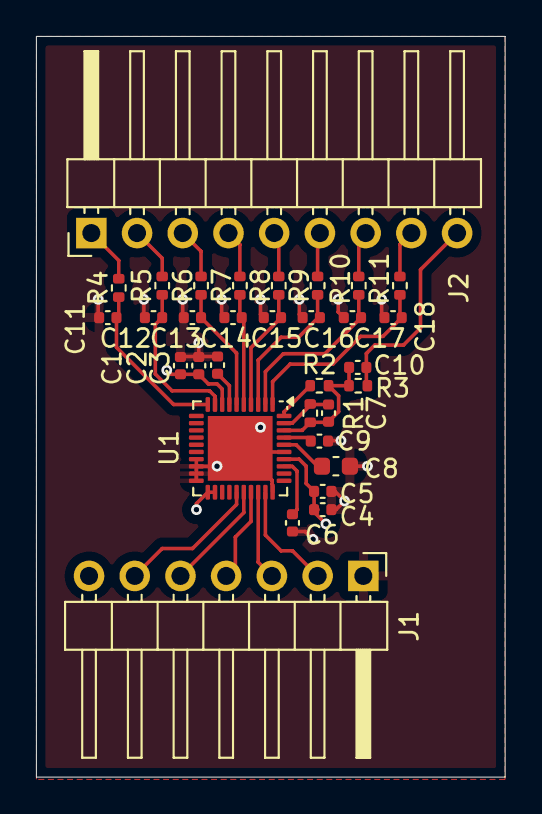
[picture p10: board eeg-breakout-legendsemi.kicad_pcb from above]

Board: 4 copper layers, 26.0 x 41.1 mm, 32 parts (0 on the bottom side), 31 nets.

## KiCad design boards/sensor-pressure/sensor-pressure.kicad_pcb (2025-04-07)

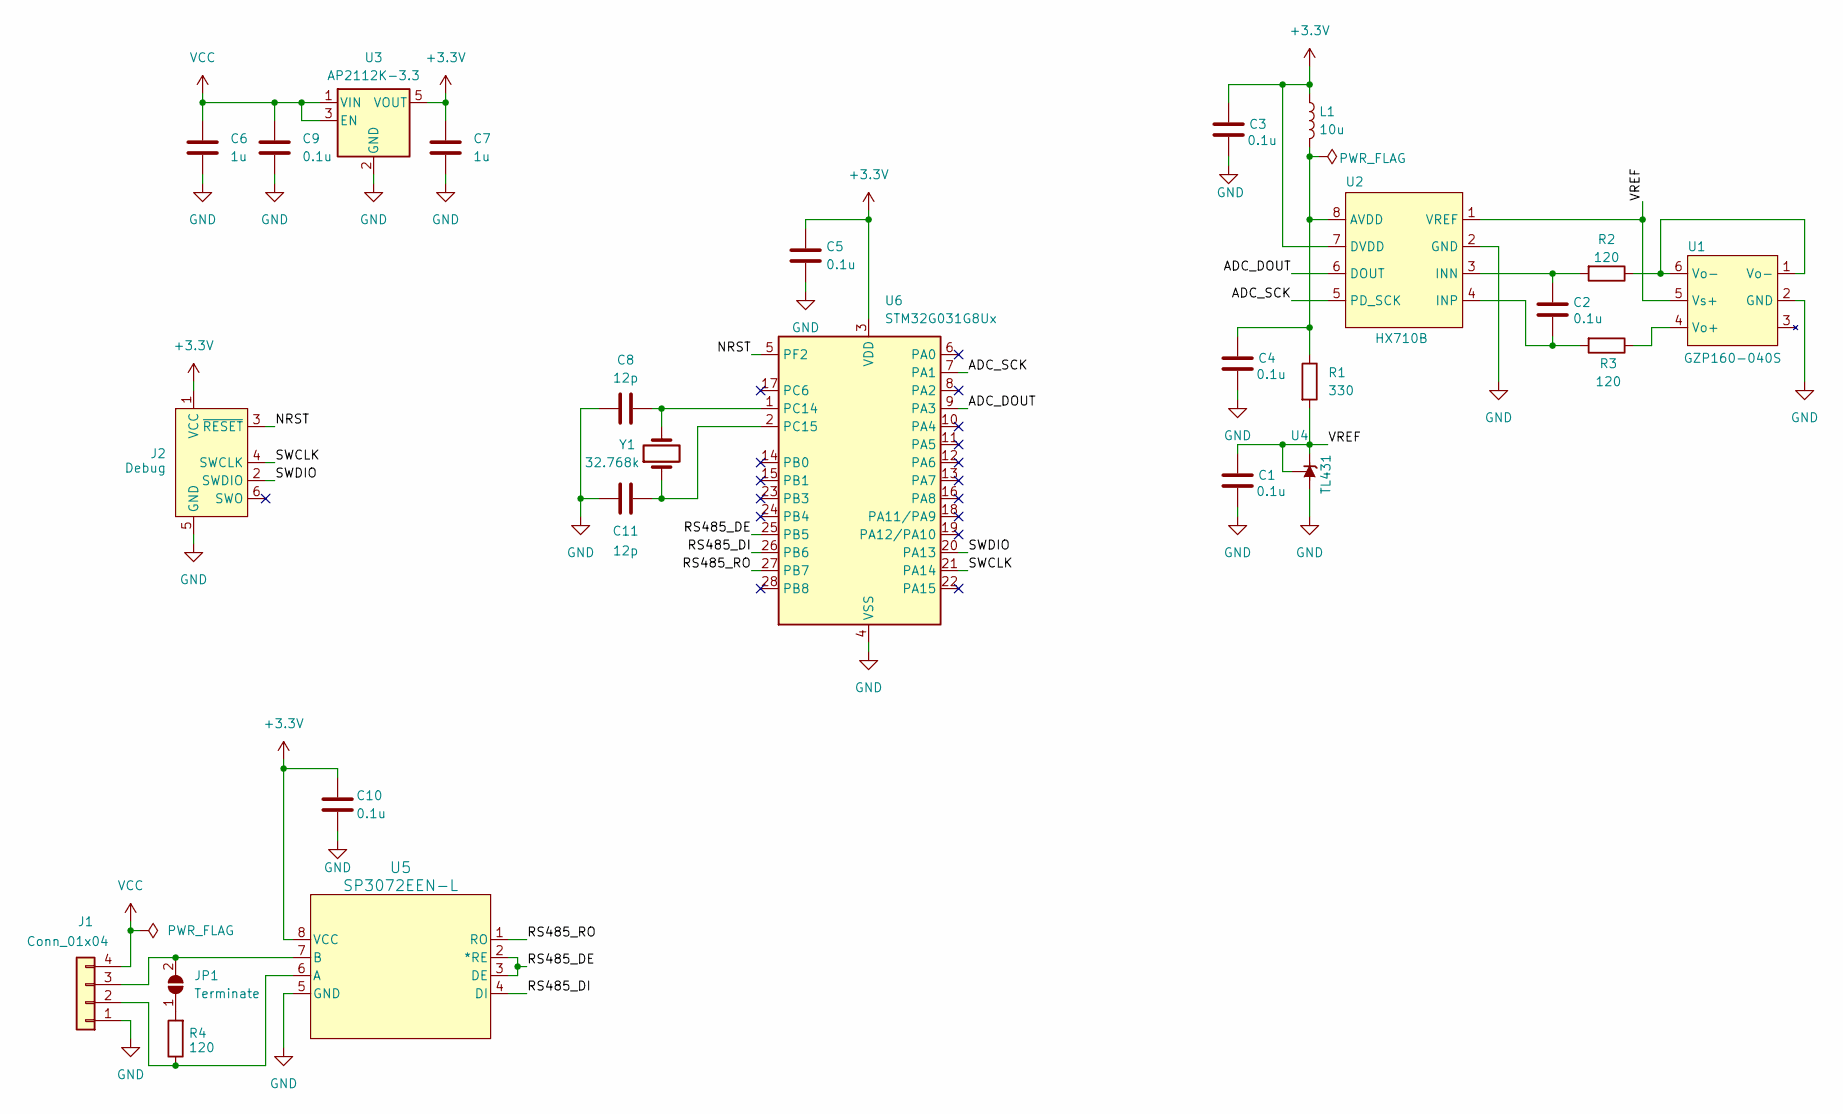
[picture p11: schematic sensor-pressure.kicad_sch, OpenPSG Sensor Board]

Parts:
C1, C2, C3, C4, C5, C9, C10: 0.1u; C_0402_1005Metric; LCSC PN C1525
C6, C7: 1u; C_0402_1005Metric; LCSC PN C52923
C8, C11: 12p; C_0402_1005Metric; LCSC PN C1547
J1: Conn_01x04; JST_PH_S4B-PH-K_1x04_P2.00mm_Horizontal; LCSC PN C2908636
J2: Debug; Tag-Connect_TC2030-IDC-NL_2x03_P1.27mm_Vertical
JP1: Terminate; SolderJumper-2_P1.3mm_Open_RoundedPad1.0x1.5mm
L1: 10u; L_0805_2012Metric; LCSC PN C1046
R1: 330; R_0402_1005Metric; LCSC PN C25104
R2, R3, R4: 120; R_0402_1005Metric; LCSC PN C25079
U1: GZP160-040S; LCSC PN C3037979
U2: HX710B; SOP-8_3.9x4.9mm_P1.27mm; LCSC PN C68417
U3: AP2112K-3.3; SOT-23-5; LCSC PN C51118
U4: TL431; SOT-23; LCSC PN C23892
U5: SP3072EEN-L; SOP-8_3.9x4.9mm_P1.27mm; LCSC PN C2692300
U6: STM32G031G8Ux; QFN-28_4x4mm_P0.5mm; LCSC PN C432211
Y1: 32.768k; Crystal_SMD_3215-2Pin_3.2x1.5mm; LCSC PN C32346

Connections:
+3.3V: C3.1, C5.1, C7.1, C10.1, J2.1 (VCC), L1.1, U2.7 (DVDD), U3.5 (VOUT), U5.8 (VCC), U6.3 (VDD)
/ADC_DOUT: U2.6 (DOUT), U6.9 (PA3)
/ADC_SCK: U2.5 (PD_SCK), U6.7 (PA1)
/NRST: J2.3 (~RESET), U6.5 (PF2)
/RS485_DE: U5.2 (*RE), U5.3 (DE), U6.25 (PB5)
/RS485_DI: U5.4 (DI), U6.26 (PB6)
/RS485_RO: U5.1 (RO), U6.27 (PB7)
/SWCLK: J2.4 (SWCLK), U6.21 (PA14)
/SWDIO: J2.2 (SWDIO), U6.20 (PA13)
/VREF: C1.1, R1.2, U1.5 (Vs+), U2.1 (VREF), U4.1 (K), U4.2 (REF)
GND: C1.2, C3.2, C4.2, C5.2, C6.2, C7.2, C8.2, C9.2, C10.2, C11.1, J1.1, J2.5 (GND), U1.2 (GND), U2.2 (GND), U3.2 (GND), U4.3 (A), U5.5 (GND), U6.4 (VSS)
unnamed: J1.2, R4.1, U5.6 (A)
unnamed: J1.3, JP1.2 (B), U5.7 (B)
unnamed: JP1.1 (A), R4.2
unnamed: R2.1, U1.1 (Vo-), U1.6 (Vo-)
unnamed: R3.1, U1.4 (Vo+)
unnamed: C4.1, L1.2, R1.1, U2.8 (AVDD)
unnamed: C2.1, R2.2, U2.3 (INN)
unnamed: C2.2, R3.2, U2.4 (INP)
unnamed: C8.1, U6.1 (PC14), Y1.2
unnamed: C11.2, U6.2 (PC15), Y1.1
VCC: C6.1, C9.1, J1.4, U3.1 (VIN), U3.3 (EN)

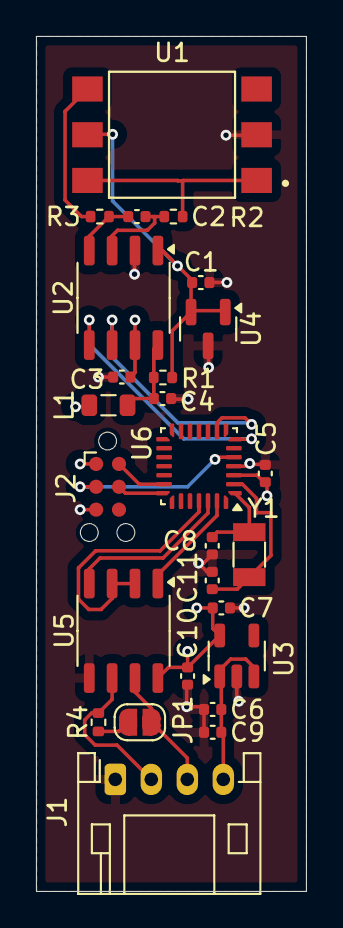
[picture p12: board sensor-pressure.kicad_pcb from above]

Board: 4 copper layers, 15.0 x 47.5 mm, 26 parts (0 on the bottom side), 22 nets.

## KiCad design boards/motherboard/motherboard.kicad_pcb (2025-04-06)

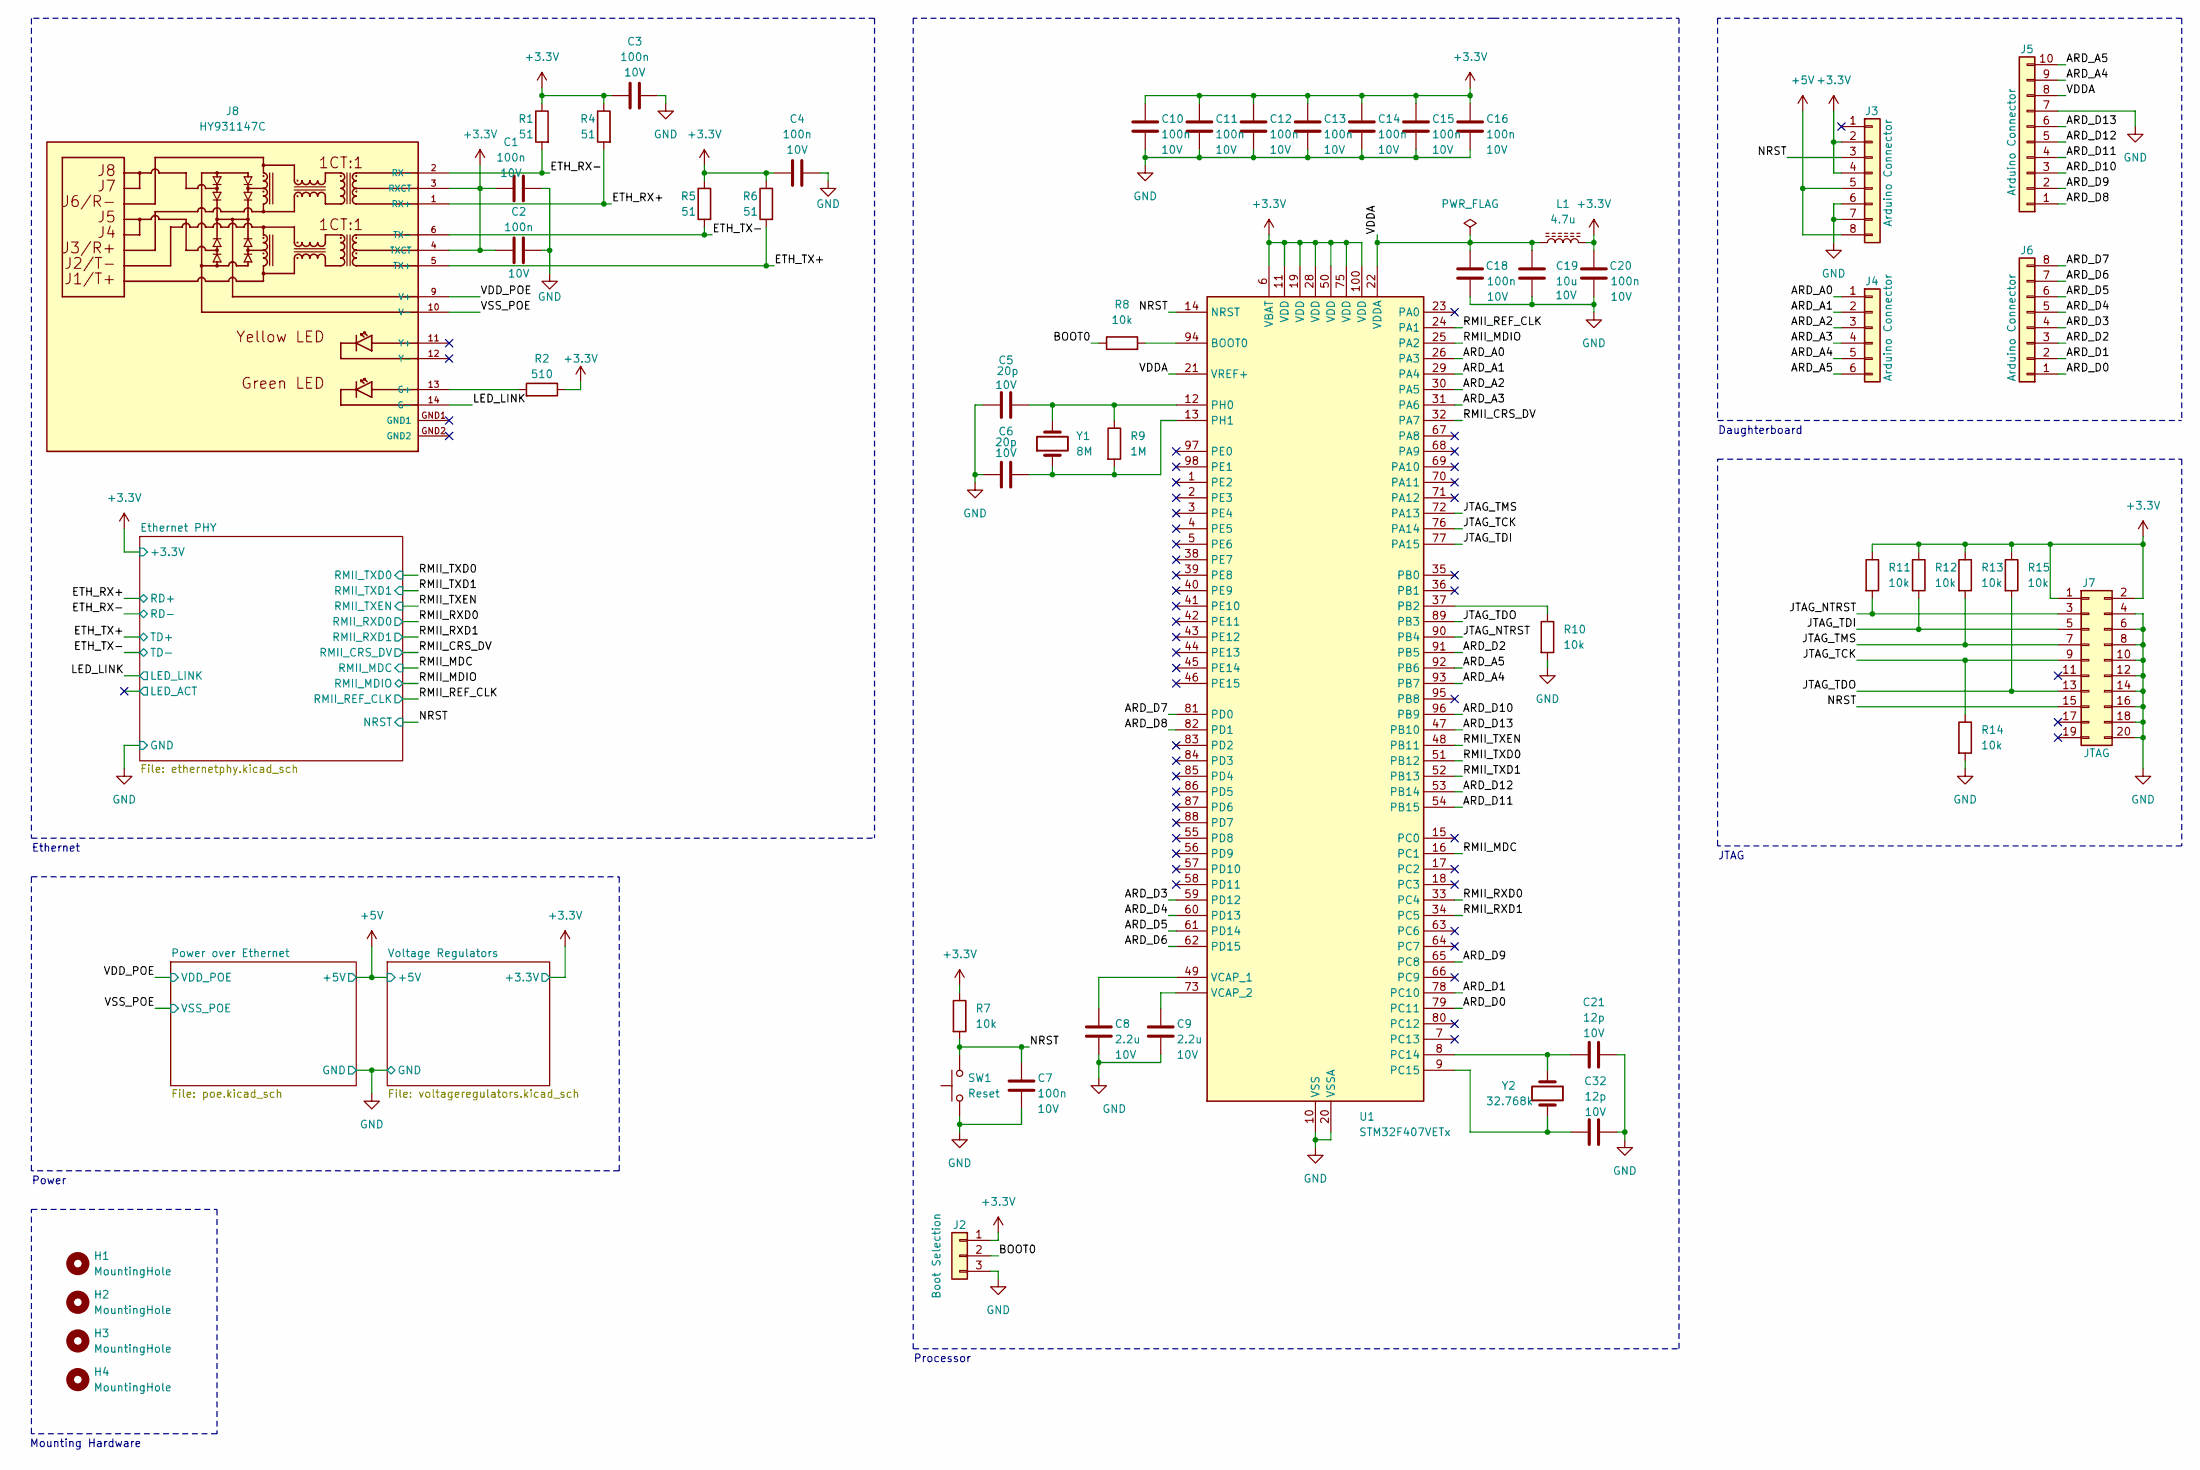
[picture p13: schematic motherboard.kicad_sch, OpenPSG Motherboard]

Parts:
C1, C2, C3, C4, C7, C10, C11, C12, C13, C14, C15, C16, C18, C20: 100n; C_0603_1608Metric; Voltage Rating 10V; LCSC PN C14663
C5, C6: 20p; C_0603_1608Metric; Voltage Rating 10V; LCSC PN C1648
C8, C9: 2.2u; C_0603_1608Metric; Voltage Rating 10V; LCSC PN C23630
C19: 10u; C_0603_1608Metric; Voltage Rating 10V; LCSC PN C96446
C21, C32: 12p; C_0603_1608Metric; Voltage Rating 10V; LCSC PN C38523
H1, H2, H3, H4: MountingHole; MountingHole_3.2mm_M3
J2: Boot Selection; PinHeader_1x03_P2.54mm_Vertical; LCSC PN C2937625
J3, J6: Arduino Connector; PinSocket_1x08_P2.54mm_Vertical; LCSC PN C2897371
J4: Arduino Connector; PinSocket_1x06_P2.54mm_Vertical; LCSC PN C2897369
J5: Arduino Connector; PinSocket_1x10_P2.54mm_Vertical; LCSC PN C2897373
J7: JTAG; IDC-Header_2x10_P2.54mm_Vertical; LCSC PN C5372868
J8: HY931147C; LCSC PN C91754
L1: 4.7u; L_0805_2012Metric; LCSC PN C86088
R1, R4, R5, R6: 51; R_0603_1608Metric; LCSC PN C23197
R2: 510; R_0603_1608Metric; LCSC PN C23193
R7, R8, R10, R11, R12, R13, R14, R15: 10k; R_0603_1608Metric; LCSC PN C25804
R9: 1M; R_0603_1608Metric; LCSC PN C22935
SW1: Reset; SW_SPST_SKQG_WithStem; LCSC PN C318884
U1: STM32F407VETx; LQFP-100_14x14mm_P0.5mm; LCSC PN C28730
Y1: 8M; Crystal_SMD_5032-2Pin_5.0x3.2mm; LCSC PN C115962
Y2: 32.768k; Crystal_SMD_3215-2Pin_3.2x1.5mm; LCSC PN C32346

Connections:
+3.3V: C1.2, C2.2, C3.1, C4.1, C10.1, C11.1, C12.1, C13.1, C14.1, C15.1, C16.1, C20.1, J2.1, J3.2, J3.4, J7.1, J7.2, J8.3 (RXCT), J8.4 (TXCT), L1.1, R1.1, R2.1, R4.1, R5.1, R6.1, R7.1, R11.1, R12.1, R13.1, R15.1, U1.6 (VBAT), U1.11 (VDD), U1.19 (VDD), U1.28 (VDD), U1.50 (VDD), U1.75 (VDD), U1.100 (VDD); also elsewhere on the board
+5V: J3.5, J3.8; also elsewhere on the board
/ARD_A0: J4.1, U1.26 (PA3)
/ARD_A1: J4.2, U1.29 (PA4)
/ARD_A2: J4.3, U1.30 (PA5)
/ARD_A3: J4.4, U1.31 (PA6)
/ARD_A4: J4.5, J5.9, U1.93 (PB7)
/ARD_A5: J4.6, J5.10, U1.92 (PB6)
/ARD_D0: J6.1, U1.79 (PC11)
/ARD_D1: J6.2, U1.78 (PC10)
/ARD_D2: J6.3, U1.91 (PB5)
/ARD_D3: J6.4, U1.59 (PD12)
/ARD_D4: J6.5, U1.60 (PD13)
/ARD_D5: J6.6, U1.61 (PD14)
/ARD_D6: J6.7, U1.62 (PD15)
/ARD_D7: J6.8, U1.81 (PD0)
/ARD_D8: J5.1, U1.82 (PD1)
/ARD_D9: J5.2, U1.65 (PC8)
/ARD_D10: J5.3, U1.96 (PB9)
/ARD_D11: J5.4, U1.54 (PB15)
/ARD_D12: J5.5, U1.53 (PB14)
/ARD_D13: J5.6, U1.47 (PB10)
/BOOT0: J2.2, R8.1
/ETH_RX+: J8.1 (RX+), R4.2; also elsewhere on the board
/ETH_RX-: J8.2 (RX-), R1.2; also elsewhere on the board
/ETH_TX+: J8.5 (TX+), R6.2; also elsewhere on the board
/ETH_TX-: J8.6 (TX-), R5.2; also elsewhere on the board
/JTAG_NTRST: J7.3, R11.2, U1.90 (PB4)
/JTAG_TCK: J7.9, R14.1, U1.76 (PA14)
/JTAG_TDI: J7.5, R12.2, U1.77 (PA15)
/JTAG_TDO: J7.13, R15.2, U1.89 (PB3)
/JTAG_TMS: J7.7, R13.2, U1.72 (PA13)
/LED_LINK: J8.14 (G-); also elsewhere on the board
/NRST: C7.1, J3.3, J7.15, R7.2, SW1.1, U1.14 (NRST); also elsewhere on the board
/RMII_CRS_DV: U1.32 (PA7); also elsewhere on the board
/RMII_MDC: U1.16 (PC1); also elsewhere on the board
/RMII_MDIO: U1.25 (PA2); also elsewhere on the board
/RMII_REF_CLK: U1.24 (PA1); also elsewhere on the board
/RMII_RXD0: U1.33 (PC4); also elsewhere on the board
/RMII_RXD1: U1.34 (PC5); also elsewhere on the board
/RMII_TXD0: U1.51 (PB12); also elsewhere on the board
/RMII_TXD1: U1.52 (PB13); also elsewhere on the board
/RMII_TXEN: U1.48 (PB11); also elsewhere on the board
/VDDA: C18.1, C19.1, J5.8, L1.2, U1.21 (VREF+), U1.22 (VDDA)
/VDD_POE: J8.9 (V+); also elsewhere on the board
/VSS_POE: J8.10 (V-); also elsewhere on the board
GND: C1.1, C2.1, C3.2, C4.2, C5.1, C6.1, C7.2, C8.2, C9.2, C10.2, C11.2, C12.2, C13.2, C14.2, C15.2, C16.2, C18.2, C19.2, C20.2, C21.2, C32.2, J2.3, J3.6, J3.7, J5.7, J7.4, J7.6, J7.8, J7.10, J7.12, J7.14, J7.16, J7.18, J7.20, R10.2, R14.2, SW1.2, U1.10 (VSS), U1.20 (VSSA), U1.27 (VSS), U1.74 (VSS), U1.99 (VSS); also elsewhere on the board
unnamed: J8.13 (G+), R2.2
unnamed: R8.2, U1.94 (BOOT0)
unnamed: R10.1, U1.37 (PB2)
unnamed: C21.1, U1.8 (PC14), Y2.2
unnamed: C32.1, U1.9 (PC15), Y2.1
unnamed: C5.2, R9.1, U1.12 (PH0), Y1.2
unnamed: C6.2, R9.2, U1.13 (PH1), Y1.1
unnamed: C8.1, U1.49 (VCAP_1)
unnamed: C9.1, U1.73 (VCAP_2)

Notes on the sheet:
Mounting Hardware
Power
JTAG
Processor
Daughterboard
Ethernet

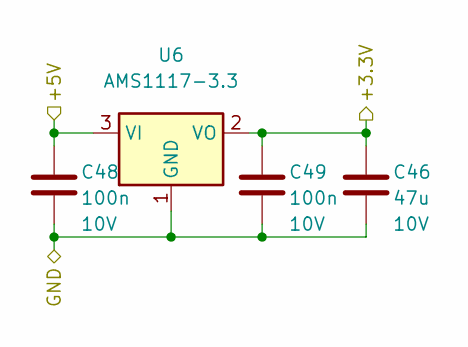
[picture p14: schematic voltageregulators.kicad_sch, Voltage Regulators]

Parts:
C46: 47u; C_1206_3216Metric; Voltage Rating 10V; LCSC PN C96123
C48, C49: 100n; C_0603_1608Metric; Voltage Rating 10V; LCSC PN C14663
U6: AMS1117-3.3; SOT-223-3_TabPin2; LCSC PN C6186

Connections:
+3.3V: C46.1, C49.1, U6.2 (VO); also elsewhere on the board
+5V: C48.1, U6.3 (VI); also elsewhere on the board
GND: C46.2, C48.2, C49.2, U6.1 (GND); also elsewhere on the board

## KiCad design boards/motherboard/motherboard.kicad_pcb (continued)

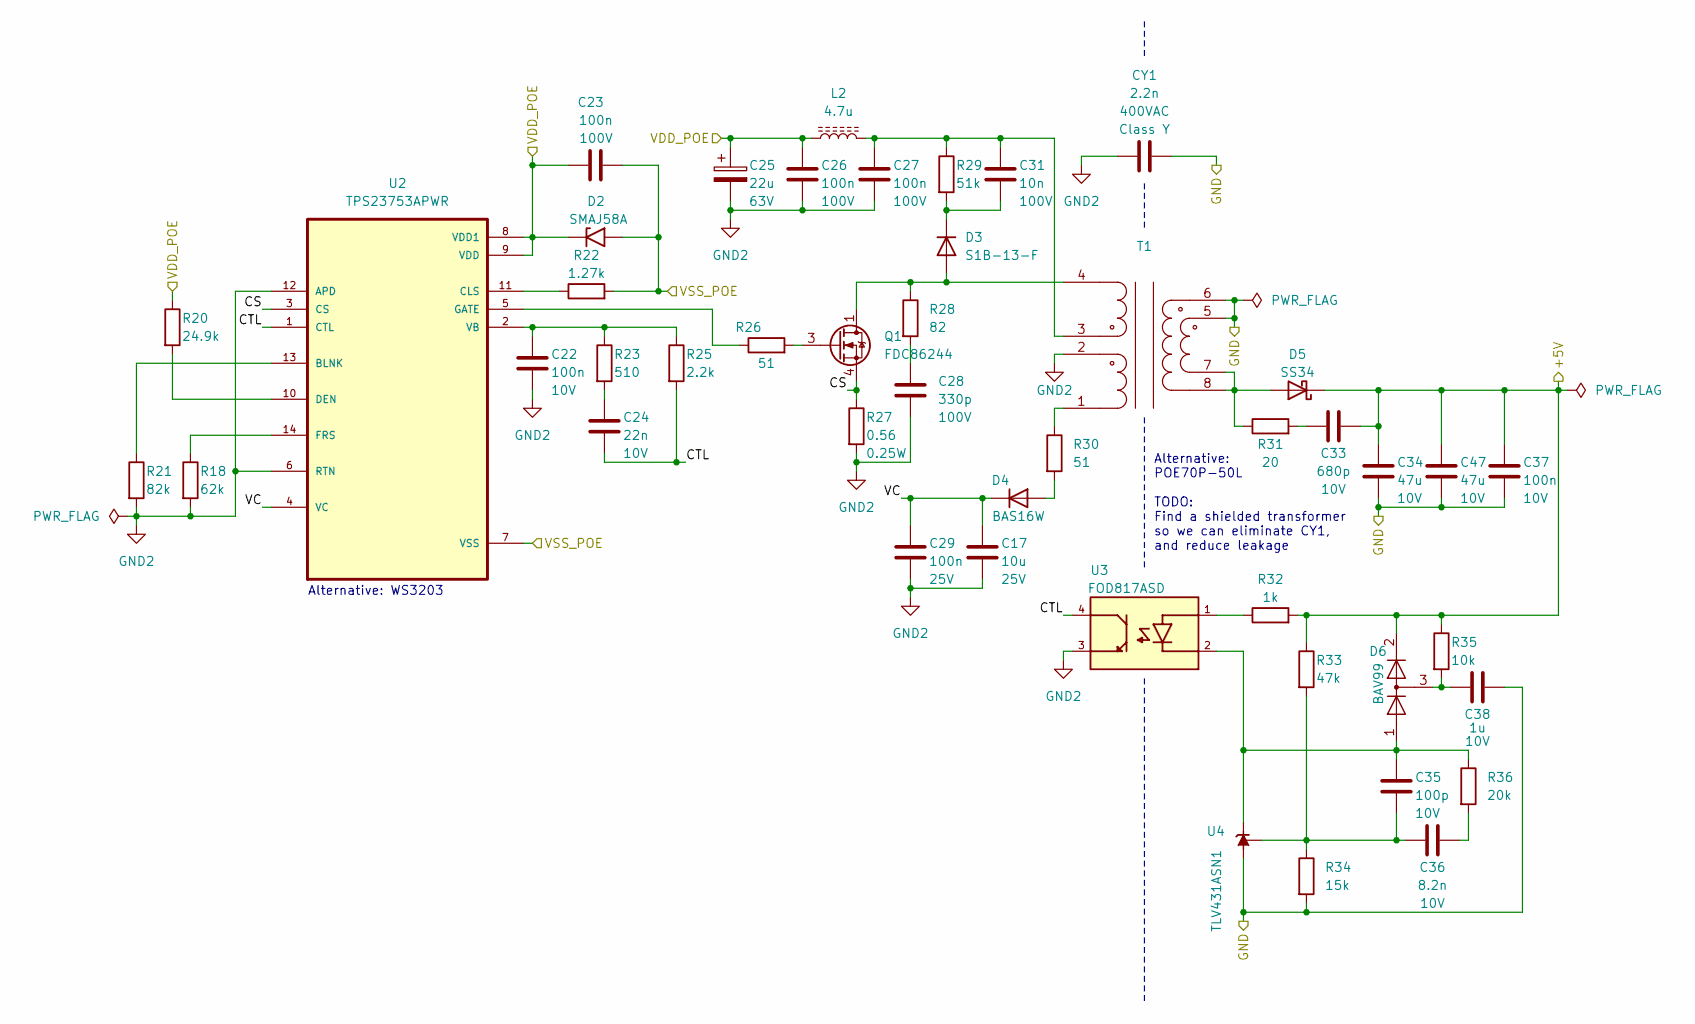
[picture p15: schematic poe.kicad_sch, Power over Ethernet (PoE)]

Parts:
C17: 10u; C_0603_1608Metric; Voltage Rating 25V; LCSC PN C96446
C22, C37: 100n; C_0603_1608Metric; Voltage Rating 10V; LCSC PN C14663
C23, C26, C27: 100n; C_0805_2012Metric; Voltage Rating 100V; LCSC PN C28233
C24: 22n; C_0603_1608Metric; Voltage Rating 10V; LCSC PN C21122
C25: 22u; CP_Elec_6.3x7.7; Voltage Rating 63V; LCSC PN C267472
C28: 330p; C_0603_1608Metric; Voltage Rating 100V; LCSC PN C126579
C29: 100n; C_0603_1608Metric; Voltage Rating 25V; LCSC PN C14663
C31: 10n; C_0603_1608Metric; Voltage Rating 100V; LCSC PN C107059
C33: 680p; C_0603_1608Metric; Voltage Rating 10V; LCSC PN C1630
C34, C47: 47u; C_1206_3216Metric; Voltage Rating 10V; LCSC PN C96123
C35: 100p; C_0603_1608Metric; Voltage Rating 10V; LCSC PN C14858
C36: 8.2n; C_0603_1608Metric; Voltage Rating 10V; LCSC PN C1322360
C38: 1u; C_0603_1608Metric; Voltage Rating 10V; LCSC PN C15849
CY1: 2.2n; C_Disc_D10.5mm_W5.0mm_P10.00mm; Voltage Rating 400VAC; LCSC PN C499511
D2: SMAJ58A; D_SMA; LCSC PN C110521
D3: S1B-13-F; D_SMA; LCSC PN C156295
D4: BAS16W; SOT-323_SC-70; LCSC PN C56624
D5: SS34; D_SMA; LCSC PN C8678
D6: BAV99; SOT-23; LCSC PN C2500
L2: 4.7u; L_1008_2520Metric; LCSC PN C82314
Q1: FDC86244; SuperSOT-6; LCSC PN C3290085
R18: 82k; R_0603_1608Metric; LCSC PN C23254
R20: 24.9k; R_0603_1608Metric; LCSC PN C2930080
R21: 62k; R_0603_1608Metric; LCSC PN C23221
R22: 1.27k; R_0603_1608Metric; LCSC PN C2930048
R23: 510; R_0603_1608Metric; LCSC PN C23193
R25: 2.2k; R_0603_1608Metric; LCSC PN C4190
R26, R30: 51; R_0603_1608Metric; LCSC PN C23197
R27: 0.56; R_1206_3216Metric; Power Rating 0.25W; LCSC PN C2907358
R28: 82; R_0603_1608Metric; LCSC PN C23255
R29: 51k; R_0603_1608Metric; LCSC PN C23196
R31: 20; R_0603_1608Metric; LCSC PN C22950
R32: 1k; R_0603_1608Metric; LCSC PN C21190
R33: 47k; R_0603_1608Metric; LCSC PN C25819
R34: 15k; R_0603_1608Metric; LCSC PN C22809
R35: 10k; R_0603_1608Metric; LCSC PN C25804
R36: 20k; R_0603_1608Metric; LCSC PN C4184
T1: HR051067; XFMR-SMD_HR051067; LCSC PN C93830
U2: TPS23753APWR; TSSOP-14_4.4x5mm_P0.65mm; LCSC PN C92115
U3: FOD817ASD; SOIC254P1016X385-4N; LCSC PN C241830
U4: TLV431ASN1; SOT-23-3; LCSC PN C127592

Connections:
+5V: C33.2, C34.1, C37.1, C47.1, D5.1 (K), D6.2 (A), R32.2, R33.1, R35.1; also elsewhere on the board
/Power over Ethernet/CS: Q1.4 (S), R27.1, U2.3 (CS)
/Power over Ethernet/CTL: C24.2, R25.2, U2.1 (CTL), U3.4
/Power over Ethernet/VC: C17.1, C29.1, D4.3 (K), U2.4 (VC)
/VDD_POE: C23.1, C25.1, C26.1, D2.1 (A1), L2.1, R20.1, U2.8 (VDD1), U2.9 (VDD); also elsewhere on the board
/VSS_POE: C23.2, D2.2 (A2), R22.2, U2.7 (VSS); also elsewhere on the board
GND: C34.2, C37.2, C38.2, C47.2, CY1.1, R34.2, T1.5, T1.6, U4.3 (A); also elsewhere on the board
GND2: C17.2, C22.2, C25.2, C26.2, C27.2, C28.2, C29.2, CY1.2, R18.2, R21.2, R27.2, T1.2, U2.6 (RTN), U2.12 (APD), U3.3
unnamed: C24.1, R23.2
unnamed: C27.1, C31.1, L2.2, R29.1, T1.3
unnamed: C28.1, R28.2
unnamed: C33.1, R31.2
unnamed: C36.2, R36.2
unnamed: C38.1, D6.3 (K), R35.2
unnamed: D3.2 (A), Q1.1 (D), Q1.2 (D), Q1.5 (D), Q1.6 (D), R28.1, T1.4
unnamed: C31.2, D3.1 (K), R29.2
unnamed: D4.1 (A), R30.2
unnamed: D5.2 (A), R31.1, T1.7, T1.8
unnamed: Q1.3 (G), R26.2
unnamed: R30.1, T1.1
unnamed: R32.1, U3.1
unnamed: R18.1, U2.13 (BLNK)
unnamed: R22.1, U2.11 (CLS)
unnamed: R20.2, U2.10 (DEN)
unnamed: R21.1, U2.14 (FRS)
unnamed: R26.1, U2.5 (GATE)
unnamed: C22.1, R23.1, R25.1, U2.2 (VB)
unnamed: C35.1, D6.1 (K), R36.1, U3.2, U4.1 (K)
unnamed: C35.2, C36.1, R33.2, R34.1, U4.2 (REF)

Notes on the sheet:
Alternative: POE70P-50L TODO: Find a shielded transformer so we can eliminate CY1, and reduce leakage
Alternative: WS3203

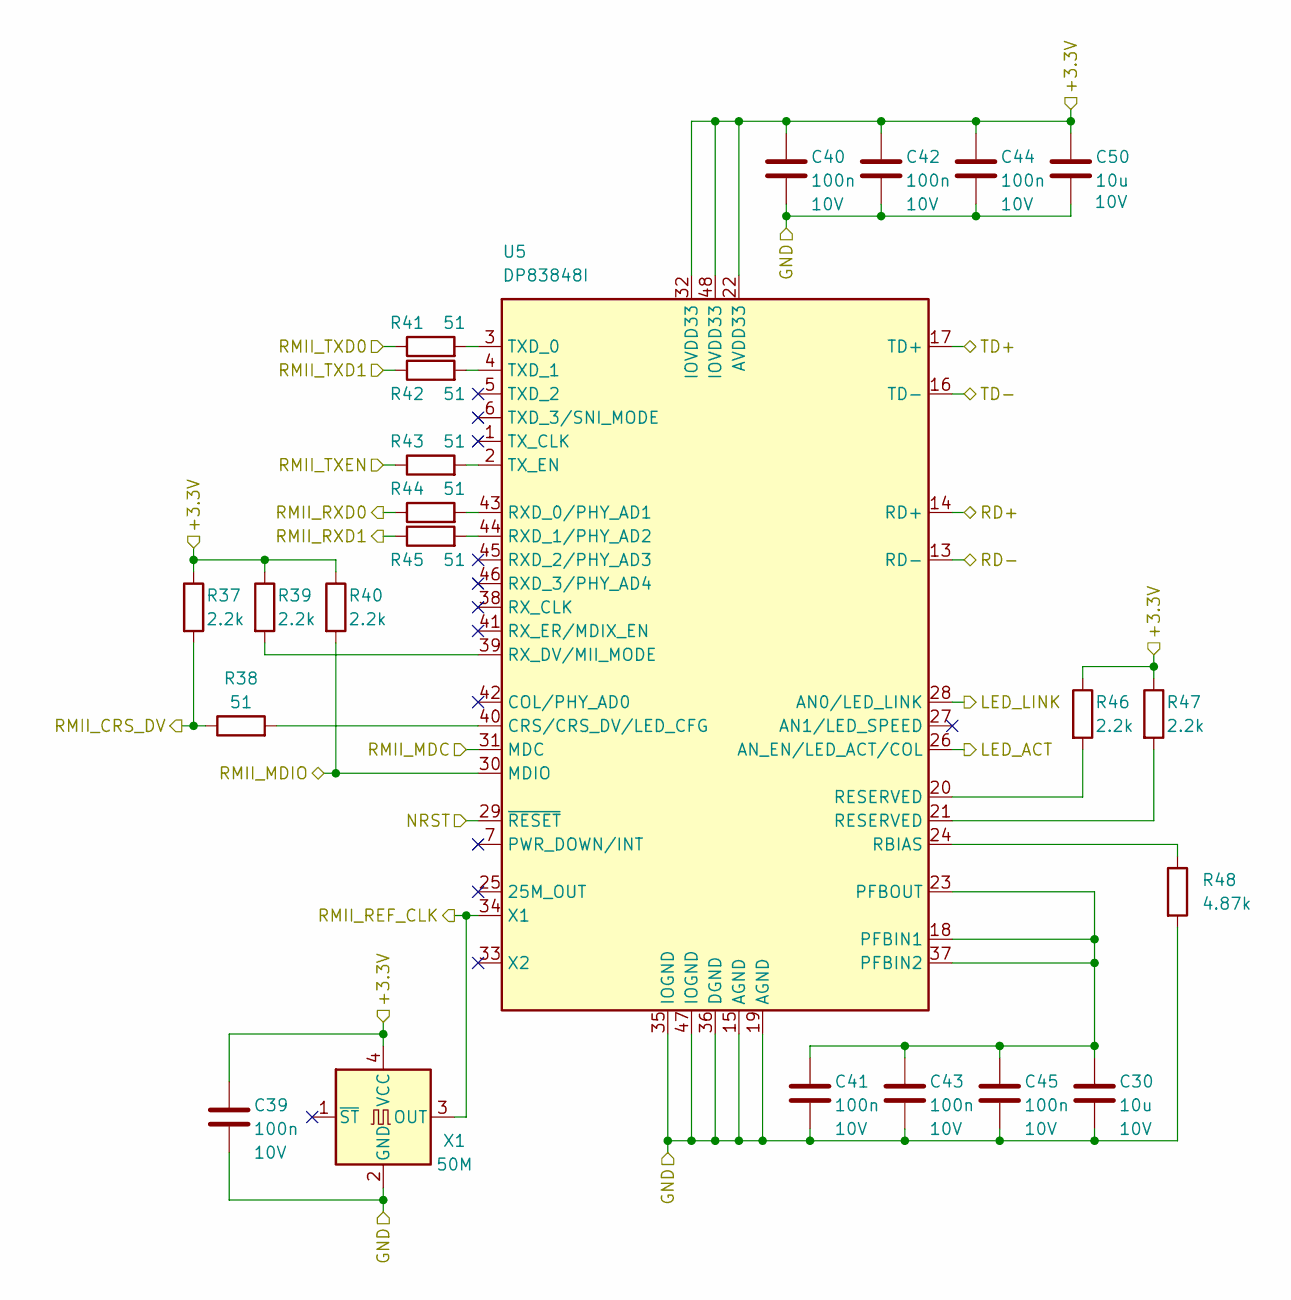
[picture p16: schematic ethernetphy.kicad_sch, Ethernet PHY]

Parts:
C30, C50: 10u; C_0603_1608Metric; Voltage Rating 10V; LCSC PN C96446
C39, C40, C41, C42, C43, C44, C45: 100n; C_0603_1608Metric; Voltage Rating 10V; LCSC PN C14663
R37, R39, R40, R46, R47: 2.2k; R_0603_1608Metric; LCSC PN C4190
R38, R41, R42, R43, R44, R45: 51; R_0603_1608Metric; LCSC PN C23197
R48: 4.87k; R_0603_1608Metric; LCSC PN C2998129
U5: DP83848I; LQFP-48_7x7mm_P0.5mm; LCSC PN C12082
X1: 50M; Oscillator_SMD_SeikoEpson_SG8002LB-4Pin_5.0x3.2mm; LCSC PN C7429728

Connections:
+3.3V: C39.1, C40.1, C42.1, C44.1, C50.1, R37.1, R39.1, R40.1, R46.1, R47.1, U5.22 (AVDD33), U5.32 (IOVDD33), U5.48 (IOVDD33), X1.4 (VCC); also elsewhere on the board
/ETH_RX+: U5.14 (RD+); also elsewhere on the board
/ETH_RX-: U5.13 (RD-); also elsewhere on the board
/ETH_TX+: U5.17 (TD+); also elsewhere on the board
/ETH_TX-: U5.16 (TD-); also elsewhere on the board
/Ethernet PHY/LED_ACT: U5.26 (AN_EN/LED_ACT/COL)
/LED_LINK: U5.28 (AN0/LED_LINK); also elsewhere on the board
/NRST: U5.29 (~RESET); also elsewhere on the board
/RMII_CRS_DV: R37.2, R38.1; also elsewhere on the board
/RMII_MDC: U5.31 (MDC); also elsewhere on the board
/RMII_MDIO: R40.2, U5.30 (MDIO); also elsewhere on the board
/RMII_REF_CLK: U5.34 (X1), X1.3 (OUT); also elsewhere on the board
/RMII_RXD0: R44.1; also elsewhere on the board
/RMII_RXD1: R45.1; also elsewhere on the board
/RMII_TXD0: R41.1; also elsewhere on the board
/RMII_TXD1: R42.1; also elsewhere on the board
/RMII_TXEN: R43.1; also elsewhere on the board
GND: C30.2, C39.2, C40.2, C41.2, C42.2, C43.2, C44.2, C45.2, C50.2, R48.2, U5.15 (AGND), U5.19 (AGND), U5.35 (IOGND), U5.36 (DGND), U5.47 (IOGND), X1.2 (GND); also elsewhere on the board
unnamed: R46.2, U5.20 (RESERVED)
unnamed: R47.2, U5.21 (RESERVED)
unnamed: R38.2, U5.40 (CRS/CRS_DV/LED_CFG)
unnamed: C30.1, C41.1, C43.1, C45.1, U5.18 (PFBIN1), U5.23 (PFBOUT), U5.37 (PFBIN2)
unnamed: R48.1, U5.24 (RBIAS)
unnamed: R44.2, U5.43 (RXD_0/PHY_AD1)
unnamed: R45.2, U5.44 (RXD_1/PHY_AD2)
unnamed: R39.2, U5.39 (RX_DV/MII_MODE)
unnamed: R41.2, U5.3 (TXD_0)
unnamed: R42.2, U5.4 (TXD_1)
unnamed: R43.2, U5.2 (TX_EN)


Board: 4 copper layers, 60.0 x 112.0 mm, 124 parts (0 on the bottom side), 92 nets.

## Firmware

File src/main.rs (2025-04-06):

/* SPDX-License-Identifier: AGPL-3.0-or-later
 *
 * Copyright (C) 2025 The OpenPSG Authors.
 *
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
 * You should have received a copy of the GNU Affero General Public License
 * along with this program.  If not, see <https://www.gnu.org/licenses/>.
 */

#![cfg_attr(not(test), no_std)]
#![cfg_attr(not(test), no_main)]

use crate::api::RpcHandler;
//use crate::cs1237::{Channel, Config as Cs1237Config, Cs1237, Gain, SamplesPerSecond};
use crate::net_util::generate_mac_address;
use crate::task::TaskSignal;
use crate::time::{clock_gettime, clock_settime, init_time, Timespec};
use core::net::{IpAddr, SocketAddr};
use core::option::Option::*;
use core::result::Result::*;
use defmt::{debug, error, info, warn};
use embassy_executor::Spawner;
use embassy_net::tcp::{Error as TcpReadError, TcpSocket};
use embassy_net::udp::{PacketMetadata, UdpSocket};
use embassy_net::{Stack, StackResources};
use embassy_stm32::eth::generic_smi::GenericSMI;
use embassy_stm32::eth::{Ethernet, PacketQueue};
use embassy_stm32::peripherals::ETH;
use embassy_stm32::rng::Rng;
use embassy_stm32::time::Hertz;
use embassy_stm32::{bind_interrupts, eth, peripherals, rng, Config};
use embassy_sync::blocking_mutex::raw::ThreadModeRawMutex;
use embassy_sync::signal::Signal as EmbassySignal;
use embassy_time::{Duration, Timer};
use embedded_jsonrpc::RpcServer;
use rand_core::RngCore;
use static_cell::StaticCell;
use {defmt_rtt as _, panic_probe as _};

mod api;
mod biquad_filter;
mod cs1237;
mod ncpt;
mod net_util;
mod task;
mod time;

bind_interrupts!(struct Irqs {
    ETH => eth::InterruptHandler;
    RNG => rng::InterruptHandler<peripherals::RNG>;
});

type Device = Ethernet<'static, ETH, GenericSMI>;

const NTP_PORT: u16 = 123;
const NTP_PACKET_SIZE: usize = 48;

#[embassy_executor::task]
async fn net_task(mut runner: embassy_net::Runner<'static, Device>) -> ! {
    runner.run().await
}

#[embassy_executor::task]
async fn timesync_task(stack: Stack<'static>) -> ! {
    let timestamp_gen = TimestampGen::default();
    let context = sntpc::NtpContext::new(timestamp_gen);

    let mut rx_meta = [PacketMetadata::EMPTY; 1];
    let mut rx_buffer = [0; NTP_PACKET_SIZE];
    let mut tx_meta = [PacketMetadata::EMPTY; 1];
    let mut tx_buffer = [0; NTP_PACKET_SIZE];

    let mut socket = UdpSocket::new(
        stack,
        &mut rx_meta,
        &mut rx_buffer,
        &mut tx_meta,
        &mut tx_buffer,
    );
    socket.bind(NTP_PORT).unwrap();

    // Get the address of the network gateway.
    let gateway = stack.config_v4().unwrap().gateway;
    if gateway.is_none() {
        panic!("Expected a gateway address");
    }

    let ntp_addr = SocketAddr::new(IpAddr::V4(gateway.unwrap()), NTP_PORT);

    loop {
        match sntpc::get_time(ntp_addr, &socket, context).await {
            Ok(time) => {
                clock_settime(&Timespec {
                    seconds: time.sec() as u64,
                    micros: (u64::from(time.sec_fraction()) * 1_000_000 / u64::from(u32::MAX))
                        as u32,
                })
                .unwrap();

                debug!("Time synchronized: {:?}", time);
            }
            Err(err) => {
                error!("Time synchronization error: {:?}", err);
            }
        }

        Timer::after(Duration::from_secs(20)).await;
    }
}

#[embassy_executor::main]
async fn main(spawner: Spawner) -> ! {
    debug!("Starting...");

    let mut config = Config::default();
    {
        use embassy_stm32::rcc::*;
        config.rcc.hse = Some(Hse {
            freq: Hertz(8_000_000),
            mode: HseMode::Oscillator,
        });
        config.rcc.pll_src = PllSource::HSE;
        config.rcc.pll = Some(Pll {
            prediv: PllPreDiv::DIV8,
            mul: PllMul::MUL336,
            divp: Some(PllPDiv::DIV2), // 8mhz / 8 * 336 / 2 = 168Mhz.
            divq: Some(PllQDiv::DIV7), // 8mhz / 8 * 336 / 7 = 48Mhz.
            divr: None,
        });
        config.rcc.ahb_pre = AHBPrescaler::DIV1;
        config.rcc.apb1_pre = APBPrescaler::DIV4;
        config.rcc.apb2_pre = APBPrescaler::DIV2;
        config.rcc.sys = Sysclk::PLL1_P;
        config.rcc.ls = LsConfig::default_lse();
    }

    debug!("Initializing clocks...");

    let p = embassy_stm32::init(config);

    // Initialize peripherals
   /*  let ncpt_adc = Cs1237::try_new(
        p.SPI1,
        p.PA5,
        p.PA6,
        p.DMA2_CH3,
        p.DMA2_CH2,
        p.EXTI6,
        Cs1237Config {
            sample_rate: SamplesPerSecond::SPS40,
            gain: Gain::G128,
            channel: Channel::ChannelA,
        },
    )
    .await
    .unwrap();
*/
    // Initialize the RTC.
    debug!("Initializing RTC...");
    init_time(p.RTC);

    // Generate random seed.
    debug!("Generating random ethernet seed...");
    let mut rng = Rng::new(p.RNG, Irqs);
    let mut seed = [0; 8];
    rng.fill_bytes(&mut seed);
    let seed = u64::from_le_bytes(seed);

    // Initialize Ethernet device.
    debug!("Initializing Ethernet device...");
    let mac_addr = generate_mac_address();

    static PACKETS: StaticCell<PacketQueue<4, 4>> = StaticCell::new();
    let packet_queue = PACKETS.init(PacketQueue::<4, 4>::new());

    debug!("Bringing up Ethernet device...");

    let device = Ethernet::new(
        packet_queue,
        p.ETH,
        Irqs,
        p.PA1,
        p.PA2,
        p.PC1,
        p.PA7,
        p.PC4,
        p.PC5,
        p.PB12,
        p.PB13,
        p.PB11,
        GenericSMI::new(1), // The default dp83848 address is "1" unlike the LAN8742 which is "0".
        mac_addr,
    );

    // Acquire network configuration using DHCP.
    let config = embassy_net::Config::dhcpv4(embassy_net::DhcpConfig::default());

    // Init network stack
    static RESOURCES: StaticCell<StackResources<3>> = StaticCell::new();
    let (stack, runner) =
        embassy_net::new(device, config, RESOURCES.init(StackResources::new()), seed);

    // Launch network task
    spawner.spawn(net_task(runner)).unwrap();

    // Ensure DHCP configuration is up before trying connect
    stack.wait_config_up().await;

    // Begin synchronizing time with NTP server.
    spawner.spawn(timesync_task(stack)).unwrap();

    // Create JSON-RPC server
    static RPC_SERVER: StaticCell<RpcServer<'static, TcpReadError>> = StaticCell::new();
    let rpc_server = RPC_SERVER.init_with(RpcServer::new);

    // Task signals.
    static NCPT_SAMPLING_TASK_SIGNALS: StaticCell<EmbassySignal<ThreadModeRawMutex, TaskSignal>> =
        StaticCell::new();
    let ncpt_sampling_task_signals = NCPT_SAMPLING_TASK_SIGNALS.init_with(EmbassySignal::new);

    // Register handlers.
    static RPC_HANDLER: StaticCell<RpcHandler> = StaticCell::new();
    let rpc_handler = RPC_HANDLER.init_with(|| RpcHandler::new(ncpt_sampling_task_signals));

    rpc_server
        .register_handler("openpsg.*", rpc_handler)
        .unwrap();

    // Launch pressure transducer sampling task.
  /*  spawner
        .spawn(ncpt::sample(
            rpc_server,
            ncpt_sampling_task_signals,
            ncpt_adc,
        ))
        .unwrap();
 */
    let mut rx_buffer = [0; 128]; // Received commands are nice and small.
    let mut tx_buffer = [0; 1460]; // One Ethernet frame worth of data.

    loop {
        let mut socket = TcpSocket::new(stack, &mut rx_buffer, &mut tx_buffer);
        socket.set_timeout(Some(embassy_time::Duration::from_secs(10)));
        socket.set_keep_alive(Some(embassy_time::Duration::from_secs(5)));

        if let Err(e) = socket.accept(80).await {
            warn!("Accept error: {:?}", e);
            continue;
        }

        info!(
            "Received connection from {:?}",
            socket.remote_endpoint().unwrap()
        );

        // Serve the JSON-RPC requests on the socket
        if let Err(e) = rpc_server.serve(&mut socket).await {
            warn!("JSON-RPC error: {:?}", e);
        }

        info!("Connection closed");
    }
}

#[derive(Clone, Copy, Default)]
struct TimestampGen {
    now: u64,
    now_micros: u32,
}

impl sntpc::NtpTimestampGenerator for TimestampGen {
    fn init(&mut self) {
        let tp = clock_gettime().unwrap();
        self.now = tp.seconds;
        self.now_micros = tp.micros;
    }

    fn timestamp_sec(&self) -> u64 {
        self.now
    }

    fn timestamp_subsec_micros(&self) -> u32 {
        self.now_micros
    }
}

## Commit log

2025-02-22 feat: finish motherboard circuit design
    [ethernetphy.kicad_sch, motherboard.kicad_pcb, motherboard.kicad_sch, poe.kicad_sch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]
2025-02-23 feat: assign footprints
    [ethernetphy.kicad_sch, motherboard.kicad_pcb, motherboard.kicad_sch, poe.kicad_sch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]
2025-03-11 feat: first release of motherboard
    [ethernetphy.kicad_sch, motherboard-B_Cu.gbl, motherboard-B_Mask.gbs, motherboard-B_Paste.gbp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]
2025-03-11 feat: include placements and bom
    [motherboard-all-pos.csv, motherboard-all-pos.jlcpcb.csv, motherboard-bom.csv, motherboard-bom.jlcpcb.csv]
2025-04-06 feat: revised motherboard
    [ethernetphy.kicad_sch, motherboard.kicad_pcb, motherboard.kicad_sch, poe.kicad_sch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]
2025-04-06 feat: add pressure sensor
    [sensor-pressure-B_Cu.gbl, sensor-pressure-B_Mask.gbs, sensor-pressure-B_Paste.gbp, sensor-pressure-B_Silkscreen.gbo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]
2025-04-07 feat: add movement sensor
    [sensor-movement-B_Cu.gbl, sensor-movement-B_Mask.gbs, sensor-movement-B_Paste.gbp, sensor-movement-B_Silkscreen.gbo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]
2025-04-08 feat: add eeg breakout
    [eeg-breakout-B_Cu.gbl, eeg-breakout-B_Mask.gbs, eeg-breakout-B_Paste.gbp, eeg-breakout-B_Silkscreen.gbo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]
2025-04-10 feat: tweak the eeg breakout
    [eeg-breakout.kicad_pcb, eeg-breakout.kicad_sch]
2025-04-11 feat: include legendsemi breakout
    [eeg-breakout-legendsemi-B_Cu.gbl, eeg-breakout-legendsemi-B_Mask.gbs, eeg-breakout-legendsemi-B_Paste.gbp, eeg-breakout-legendsemi-B_Silkscreen.gbo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]
2025-04-12 refactor: improve ads1292 breakout
    [eeg-breakout.kicad_pcb, eeg-breakout.kicad_sch]
2025-04-14 feat: use autodirection transceiver so stm32 bootloader can be used
    [module-base.kicad_pcb, module-base.kicad_sch]
2025-04-15 feat: add vibration motor biofeedback board
    [actuator-vibration-motor-B_Cu.gbl, actuator-vibration-motor-B_Mask.gbs, actuator-vibration-motor-B_Paste.gbp, actuator-vibration-motor-B_Silkscreen.gbo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]
2025-07-23 refactor: improve sensor config dialog
2025-07-30 feat: make tick text more compact and plan for ble scanning of difficult devices
2025-08-14 feat: add generic temperature support and revisit filters
2025-09-22 feat: move sensor type selection into its own dialog instead of multiple buttons

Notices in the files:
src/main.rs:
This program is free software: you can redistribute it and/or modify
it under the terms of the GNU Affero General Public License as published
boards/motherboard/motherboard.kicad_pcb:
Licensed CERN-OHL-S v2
